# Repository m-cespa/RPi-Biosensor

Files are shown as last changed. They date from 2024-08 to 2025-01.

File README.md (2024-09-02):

# Python Package Installation:

(python packages were all installed to a virtual environment, see [1](https://learn.adafruit.com/python-virtual-environment-usage-on-raspberry-pi/overview) for documentation)

create a python virtual environment:
```
sudo apt install python3-venv
python3 -m venv <insert desired environment name>
```

activate your virtual environment: (here it is called 'venv')
```
source venv/bin/activate
```
once activated:
```
pip3 install adafruit-python-shell
pip3 install --upgrade adafruit-python-shell
wget https://raw.githubusercontent.com/adafruit/Raspberry-Pi-Installer-Scripts/master/raspi-blinka.py
sudo -E env PATH=$PATH python3 raspi-blinka.py
```
system will now ask to reboot, after reboot and activation of venv:
```
pip3 install adafruit-circuitpython-ads1x15 adafruit-circuitpython-ads7830 adafruit-circuitpython-tca9548a adafruit-circuitpython-bme280 ds18b20
```
if `board` module is causing issues, try:
```
python3 -m pip install --upgrade --force-reinstall adafruit-blinka
```

# Method: (for RPI Model 3B+)

(for circuit information refer to schematic diagram [here](./docs/schematic_labelled.png))

**PCA9546** (4 Channel Multiplexer):\
The multiplexer was used to connect 4 BME280's onto 1 rpi. The multiplexer's package `adafruit-circuitpython-tca9548a` was installed to initialise multiple same address i2c device access [2](https://learn.adafruit.com/adafruit-tca9548a-1-to-8-i2c-multiplexer-breakout/circuitpython-python). The `mux` object seen in the script allowes accesss to the devices connected to each of the multiplexer's 4 channels by specifying the device's multiplexer channel connection (index of the mux object) and i2c address. The PCA9546's specifications can be found here [3](https://www.adafruit.com/product/5663).

**BME280** (Pressure, Temperature, Humidity):\
The sensor's adafruit package `adafruit-circuitpython-bme280` was installed to access the sensor class' methods [4](https://pypi.org/project/adafruit-circuitpython-bme280/). The adafruit package was used rather than the standard `bme280` package as creating instances of the `BME280` class in the adafruit package automates calibration which was convenient given multiple instances were called. If using a single BME280, it can be initialised in the script following the steps given by the `bme280` package's repository [5](https://pypi.org/project/RPi.bme280/). The `smbus2` package [6](https://pypi.org/project/smbus2/) did not need to be installed for our configuration using the multiplexer and `adafruit-circuitpython-bme280` package (for the `smbus2` method, refer to [7](https://randomnerdtutorials.com/raspberry-pi-bme280-python/)). For our purposes, the i2c initialisation steps were done for the multiplexer, and for each of the 4 entires in `mux`, the `0x76` i2c address (the BME280) was specified. Each BME280 was connected to a pair of clock (SCL) and data (SDA) pins on the multiplexer. The BME280's specifications can be found here [8](https://thepihut.com/products/bme280-environmental-sensor#:~:text=A%20tiny%20sensor%20breakout%20with,3.3V%2F5V%20voltage%20levels.).

**DS18B20** (1-Wire Temperature):\
The sensor was wired to the rpi following the steps given by [9](https://www.circuitbasics.com/raspberry-pi-ds18b20-temperature-sensor-tutorial/). The sensor's package `ds18b20` was used rather than the method outlined in [10](https://www.circuitbasics.com/raspberry-pi-ds18b20-temperature-sensor-tutorial/). The `ds18b20` package was setup following the steps given in the package's github repository [11](https://github.com/rgbkrk/ds18b20). The DS18B20's specifications can be found here [12](https://thepihut.com/products/ds18b20-one-wire-digital-temperature-sensor).

**ADS1115 & ADS7830** (4-channel * 8-channel Analogue-Digital Converters):\
The sensors were daisy chained and then connected across the same SCL/SDA pins as the PCA9546. The two devices have different addresses to each other and to the PCA9546 (`0x70` for PCA9546, `0x49` for ADS1115, `0x48` for ADS7830) and can be recognised as different inputs along the same i2c pins. To check that both multiplexer (mux) and analogue-digital converters (adc) are being read by the rpi, type `sudo i2cdetect -y 1` into the terminal and the above addresses should appear. The i2c address of the ADS1115 can be altered by connecting the ADDR pin to one of GND, VIN, SDA, SCL which will change the device address to `0x48`, `0x49`, `0x4a`, `0x4b` accordingly. A similar procedure can be done for the ADS7830 [13](https://cdn-learn.adafruit.com/downloads/pdf/adafruit-ads7830-8-channel-8-bit-adc.pdf) but for the circuit here described, the default `0x48` address was opted for.

The following lines were passed into terminal (order specific) to install the `ads1x15` (ADS1115) library:
1. `pip3 install --upgrade adafruit-python-shell`
2. `wget https://raw.githubusercontent.com/adafruit/Raspberry-Pi-Installer-Scripts/master/raspi-blinka.py`
3. `python3 raspi-blinka.py`
4. `pip3 install adafruit-circuitpython-ads1x15`\

Installation of the `ads7830` library after the above steps proved simpler now that the Adafruit_Blinka library was present. The following line was passed into terminal:
`pip3 install adafruit-circuitpython-ads7830` [14](https://learn.adafruit.com/adafruit-ads7830-8-channel-8-bit-adc/circuitpython-and-python)

{NOTE: you must not pass `pip3 install board` into terminal as this `board` module is completely separate from the `adafruit-circuitpython` library and will cause conflict, the correct package is installed via `raspi.blinka`. Concurrent explicit installation of the package can cause package failure. Further documentation on installing the `adafruit` and `blinka` packages necessary for the ADS1115 can be found here [15](https://learn.adafruit.com/circuitpython-on-raspberrypi-linux/installing-circuitpython-on-raspberry-pi). If there is an issue with `board` attempt force reinstalling Blinka with `python3 -m pip install --upgrade --force-reinstall adafruit-blinka`}

The `busio` package was also installed. Either the `busio` or `board` packages can be used to initialise i2c bus connections. The `busio` package allows for explicit intialisation of an i2c connection where the clock and data i2c pins can be specified (if a non default i2c bus is being used). The `board` package's `I2C()` method (`i2c_init = board.I2C()`) on the other hand will initialise the i2c bus using the standard clock and data pins. To enable future intialisation of non-default i2c buses, the `busio` initialisation (which still requires the `board` package) was chosen.

When creating the `ADS1115` & `ADS7830` objects, the same `i2c` argument as for the PCA9546 was passed whilst the i2c address was altered as required to specify each device. The ADS1115 was initialised in the script following the steps given by [16](https://www.instructables.com/How-to-Use-ADS1115-With-the-Raspberry-Pi-Part-1/). To avoid conflict between the `ADS1115` and `ADS7830` classes, their methods are inherently different. The `ADS7830` class allows only direct reading of the 32-bit signal which requires manual conversion to a voltage value - refer to [17](https://learn.adafruit.com/adafruit-ads7830-8-channel-8-bit-adc/circuitpython-and-python).

The ADS1115's specifications can be found here [18](https://thepihut.com/products/adafruit-ads1115-16-bit-adc-4-channel-with-programmable-gain-amplifier). The ADS7830's specifications can be found here [19](https://thepihut.com/products/adafruit-ads7830-8-channel-8-bit-adc-with-i2c-stemma-qt-qwiic).

**IR EMITTER-RECEIVER**:\
To yield a proxy measurement of solution turbidity, a pair of IR emitter and IR Photodiode were used. The WL-TIRC THT Infrared Round Waterclear was selected as an emitter (datasheet: [20](https://docs.rs-online.com/c30e/A700000007241424.pdf)) and the IR T-1 3/4 PIN Silicon Photodiode as a receiver (datasheet: [21](https://docs.rs-online.com/461d/0900766b808b25c5.pdf)), to note: the photodiode is opaque to visible light. Photodiodes were positioned at 180° and 90° (and a reference photodiode for each LED to check whether it was on) on the opposing side of the reactor beakers to measure through and deflected beams accordingly. To measure only the change in voltage across the photodiodes, an op-amp differential amplifier circuit was trialled where one photodiode would be in an isolated environment and the other exposed to IR. Due to variations in the base resistances of the photodiodes, wires and resistors, this configuration resulted in non-zero base reading output and was hence not used.

**PWM STIRRER**:\
Cooling fans with magnets were used to drive magnetic stirrer beads in each reactor beaker. The `PWM_Stirrer.py` script was run in the background to `ALL_Sensors.py` to keep the stirrers rotating at a prescribed fixed velocity modulated by using Pulse Wave Modulation (PWM) through a GPIO pin. The script uses the `RPi.GPIO` package which should be pre-installed on updated versions of Raspbian - to check this refer to [22](https://sourceforge.net/p/raspberry-gpio-python/wiki/install/).

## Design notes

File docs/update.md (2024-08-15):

Ensure rpi is running latest Raspbian os which can be found [here](https://www.raspberrypi.com/software/operating-systems/). If an older version of raspbian is already installed:\
1. Check current version by passing `cat /etc/os-release` into terminal which should display something like this:\
```
PRETTY_NAME="Raspbian GNU/Linux 11 (bullseye)"
NAME="Raspbian GNU/Linux"
VERSION_ID="11"
VERSION="11 (bullseye)"
VERSION_CODENAME=bullseye
ID=raspbian
ID_LIKE=debian
HOME_URL="http://www.raspbian.org/"
SUPPORT_URL="http://www.raspbian.org/RaspbianForums"
```

2. If the RPi is running an old version of Raspbian pass the following commands:\
```
sudo apt update
sudo apt full-upgrade
```

Alternative: install a fresh version of raspbian onto a blank ssd through the RPi imager found [here](https://www.raspberrypi.com/software/)

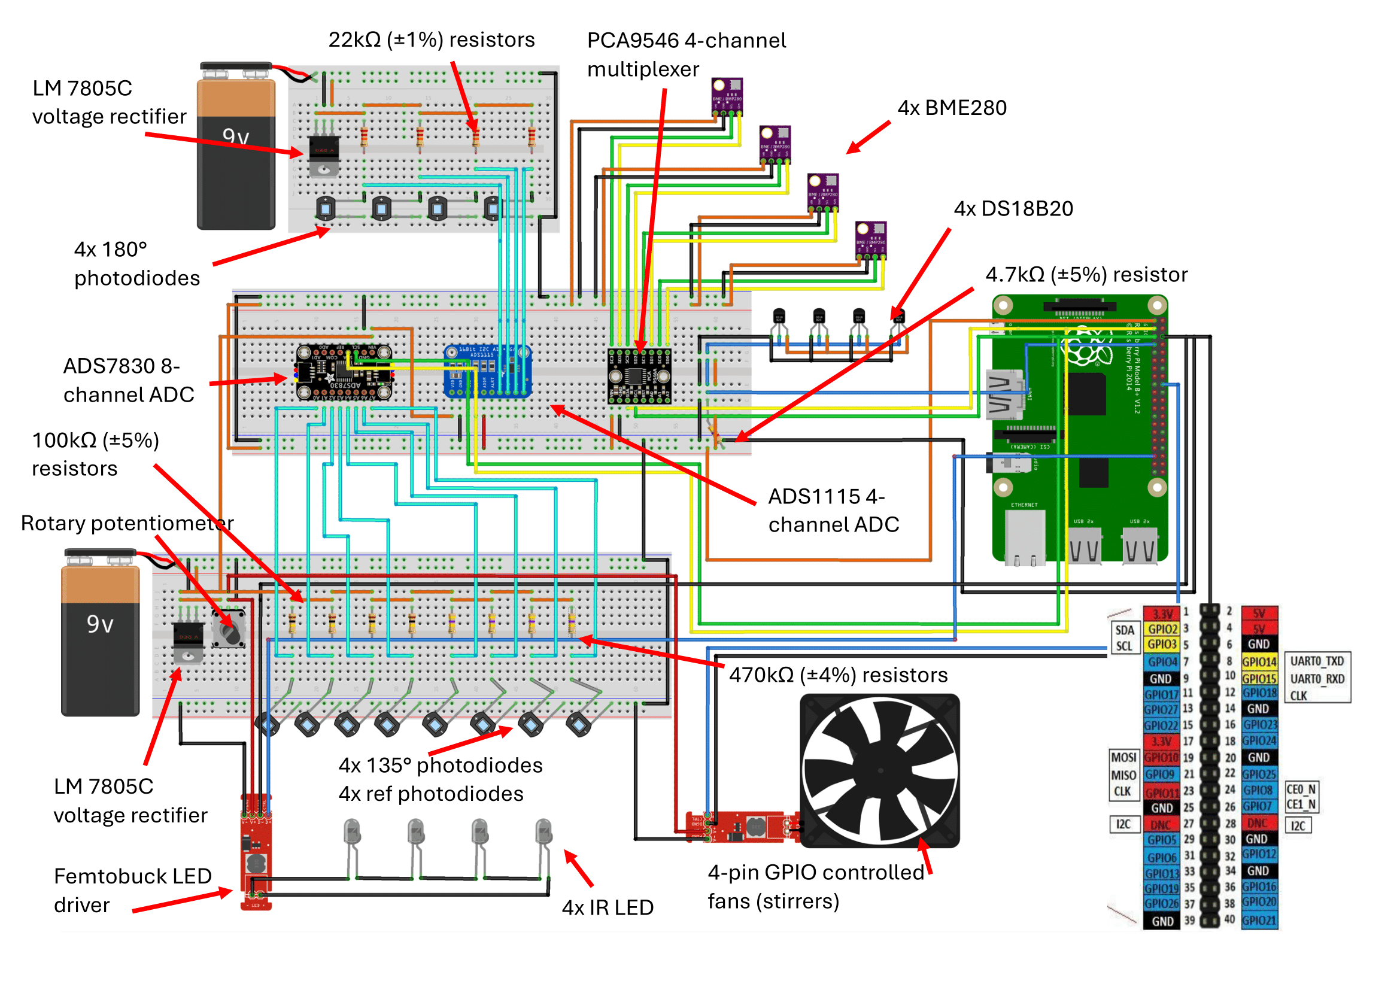
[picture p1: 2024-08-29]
docs/schematic_labelled.png

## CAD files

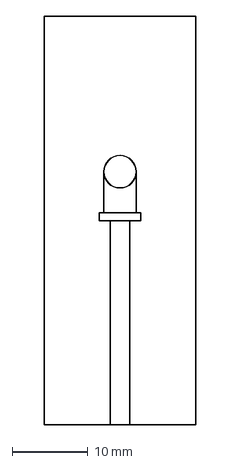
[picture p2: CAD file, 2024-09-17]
build/cad_files/photo_diode.dxf
20.0 x 54.0 mm

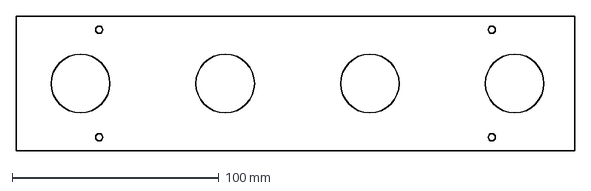
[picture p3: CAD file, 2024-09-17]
build/cad_files/lm_vial_holder.dxf
270.0 x 65.0 mm

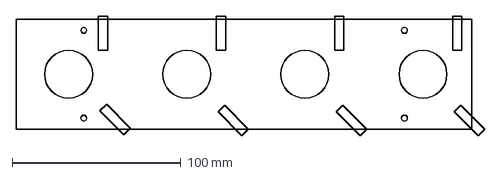
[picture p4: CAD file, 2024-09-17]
build/cad_files/higher_hole_plate.dxf
277.6 x 70.8 mm

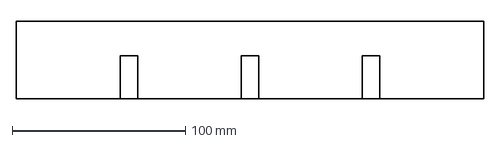
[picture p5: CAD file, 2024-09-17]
build/cad_files/slide_in_base.dxf
270.0 x 45.0 mm

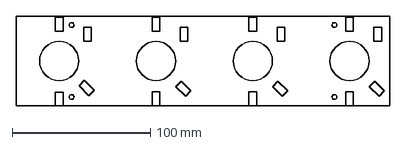
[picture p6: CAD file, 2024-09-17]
build/cad_files/top_plate_holes.dxf
270.0 x 65.0 mm

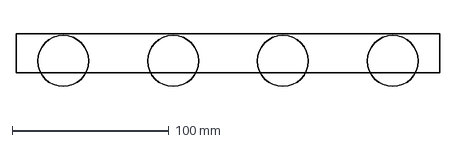
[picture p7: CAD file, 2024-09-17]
build/cad_files/light_holder.dxf
270.0 x 33.8 mm

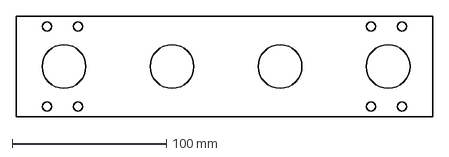
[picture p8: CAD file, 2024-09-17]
build/cad_files/lower_vial_plate.dxf
270.0 x 65.0 mm

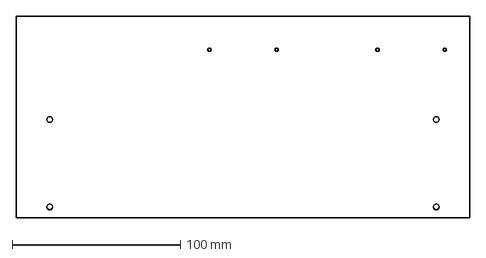
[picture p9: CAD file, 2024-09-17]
build/cad_files/clear_.base_top.dxf
270.0 x 120.0 mm

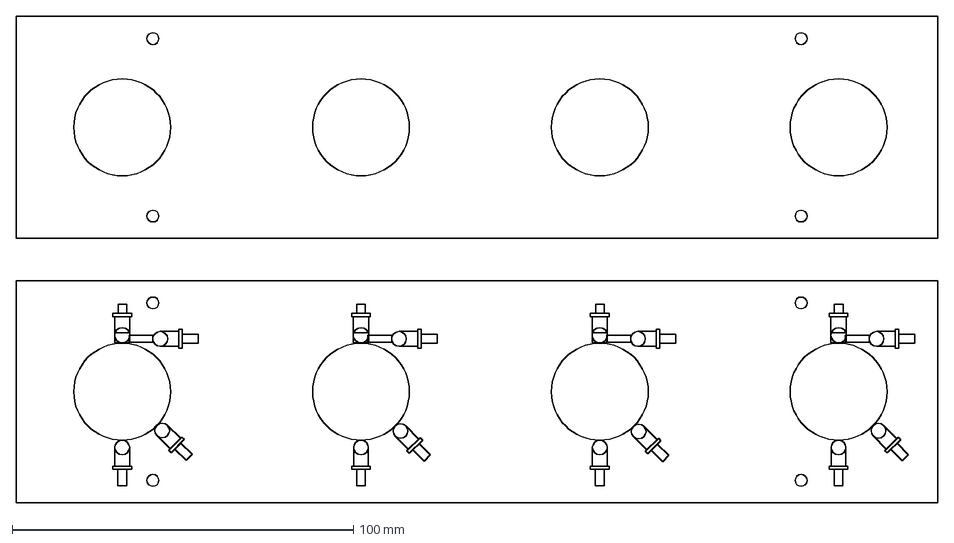
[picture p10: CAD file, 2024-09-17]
build/cad_files/photodiode_plate.dxf
270.0 x 142.5 mm

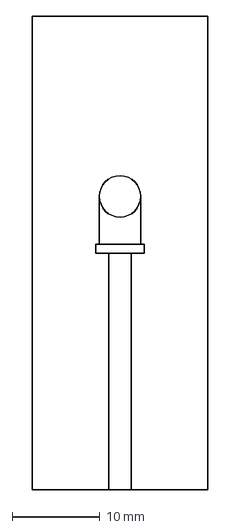
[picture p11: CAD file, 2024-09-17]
build/cad_files/LED.dxf
20.0 x 54.0 mm

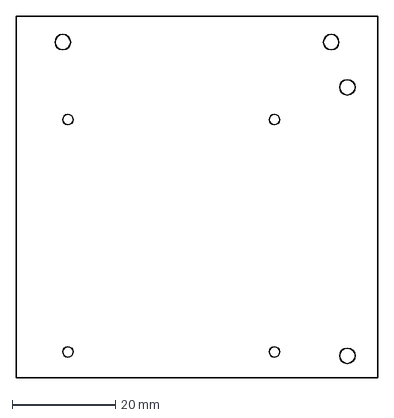
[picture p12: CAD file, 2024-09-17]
build/cad_files/pd_circuit_holder.dxf
70.0 x 70.0 mm

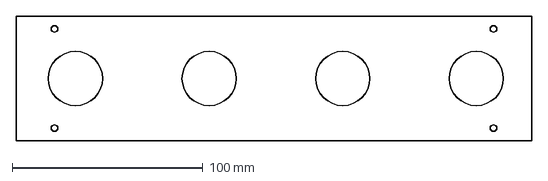
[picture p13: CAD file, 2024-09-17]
build/cad_files/therm_plate_l.dxf
270.0 x 65.0 mm

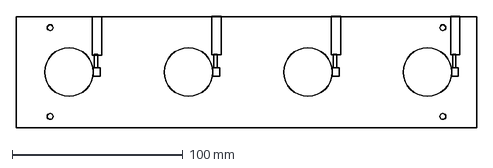
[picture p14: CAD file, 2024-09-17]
build/cad_files/therm_plate_m.dxf
270.0 x 65.1 mm

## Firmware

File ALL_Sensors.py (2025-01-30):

import time
from ds18b20 import DS18B20
from adafruit_bme280 import basic as adafruit_bme280
import board
import busio
import adafruit_ads1x15.ads1115 as ADS_1
from adafruit_ads1x15.analog_in import AnalogIn
import adafruit_ads7830.ads7830 as ADS_2
import adafruit_tca9548a
import RPi.GPIO as IO
import numpy as np
from tqdm import tqdm
from ledIO import LED_IO
import adafruit_pct2075
import matplotlib.pyplot as plt
from matplotlib.animation import FuncAnimation

# Setup the LEDs
# choosing BCM mode - other imported packages utilise it
leds = LED_IO('bcm', 37)

# MULTIPLEXER INITIALISATION
i2c = busio.I2C(board.SCL, board.SDA)
mux = adafruit_tca9548a.PCA9546A(i2c)

# init external temp sensor
#pct = adafruit_pct2075.PCT2075(i2c)
#print("Temperature: %.2f C"%pct.temperature)

# ADS1115 INITIALISATION
# through beam readings
adc_1 = ADS_1.ADS1115(address=0x49, i2c=i2c)

channels_1 = [AnalogIn(adc_1,ADS_1.P0),AnalogIn(adc_1,ADS_1.P1),
AnalogIn(adc_1,ADS_1.P2),AnalogIn(adc_1,ADS_1.P3)]

# ADS7830 INITIALISATION
# deflected and reference beam readings
adc_2 = ADS_2.ADS7830(i2c)
REF = 4.2

# BME280 INITIALISATION
bme_count = 4
bmes = [adafruit_bme280.Adafruit_BME280_I2C(mux[i], 0x76) for i in range(bme_count)]
bme_ext = adafruit_bme280.Adafruit_BME280_I2C(i2c,0x77)
print("Temperature: %.2f C"%bme_ext.temperature)

# DS18B20 INITILISATION
order = [2, 0, 3, 1]
out_temp_sensors = np.array(DS18B20.get_all_sensors())
out_temp_sensors = out_temp_sensors[order]
 
# Script start...
duration = 259200 #72 hrs
# duration = 43200 #12 hrs
# duration = 86400 #24 hrs

out_file = open('data/250130_yeast_w303_0.1xypd.txt','w')
string = """time t(s) T_{env} P_{env} T1_{ext} T2_{ext} T3_{ext} T4_{ext} 
T1 T2 T3 T4 P1 P2 P3 P4 H1 H2 H3 H4
Turb1_{180} Turb2_{180} Turb3_{180} Turb4_{180}
Turb1_{135} Turb2_{135} Turb3_{135} Turb4_{135}
Turb1_{ref} Turb2_{ref} Turb3_{ref} Turb4_{ref}"""
split = string.split()
title = ','.join(split)
out_file.write(title + '\n')


# Prepare data storage for plotting
times = []
# create empty lists to store lists of points to plot against time
vials = [[] for _ in range(5)]

# Set up the plot
plt.ion()  # Turn on interactive mode
fig, ax1 = plt.subplots(figsize=(10, 6))
live_vials = [ax1.plot([], [], label=f'Vial {i+1}')[0] for i in range(5)]

ax1.set_xlabel('Time (s)')
ax1.set_ylabel('Pressure (Vials) (mBar)')
ax1.tick_params(axis='y', labelcolor='r')

ax1.tick_params(axis='y', labelcolor='b')

plt.title('Real-time Pressure Data')
ax1.legend(loc='upper left')

# Function to update the plot
def update_plot():
    for i, line in enumerate(live_vials):
        line.set_data(times, vials[i])
    
    ax1.relim()
    ax1.autoscale_view()
    
    fig.canvas.draw()
    fig.canvas.flush_events()

with tqdm(total=duration, desc="Processing: ") as pbar:
    start = time.time()
    
    while True:
    # evaluating elapsed time at loop start effectively shifts timings by ~3s
    # this sets the time-scale at regular integer stesps
        current = time.time()
        elapsed = current - start
        
        if elapsed > (duration+1):
            print('Data recordng complete. Terminating...')
            pbar.update(duration - pbar.n)
            leds.finish()
            break
        else:
            pbar.update(elapsed - pbar.n)
            
        # turn on IR LEDs - sleep(1) to let signal settle
            leds.on()
            start_loop = time.time()
            time.sleep(1)
            try:
        # take DS18B20 readings first, reading temperature from 1-wire source file is the slowest operation
                out_temps = []
                out_temps.append(bme_ext.temperature)
                out_temps.append(bme_ext.pressure)
                for sensor in out_temp_sensors:
                    out_temps.append(sensor.get_temperature())
            # BME readings
                T_s = [bme.temperature for bme in bmes]
                P_s = [bme.pressure for bme in bmes]
                H_s = [bme.humidity for bme in bmes]
                TPH = T_s + P_s + H_s
            # voltage readings from ADCs
            # 8-channel ADC reads the raw 16-bit number, divide this by 2**8 and multiply by reference voltage (REF)
                voltages_1 = [ch.voltage for ch in channels_1]
                channels_2 = [adc_2.read(i) for i in range(8)]
                voltages_2 = [((ch / 65535.0) * REF) for ch in channels_2]
                line = f"""{current},{round(elapsed,3)},{",".join(map(str,out_temps))},{",".join(map(str,TPH))},{",".join(map(str,voltages_1))},{",".join(map(str,voltages_2))}"""
            except:
                line = f"""{round(elapsed,3)},{",".join(['NaN']*28)}"""
            finally:
                end_loop = time.time()
                
                # turn off IR LEDs
                leds.off()
                
                # Update plot data
                times.append(elapsed)
                for i, pressure in enumerate(P_s):
                    vials[i].append(pressure)
                vials[4].append(bme_ext.pressure)
            
            # Update the plot
                update_plot()
            
            # calculates correct pausing time
                diff = end_loop - start_loop
                dt = max(np.ceil(diff),diff) - diff
                pausing = dt + diff
                out_file.write(line + '\n')
                
            # sets interval between measurements
                interval = 30
                time.sleep(interval - pausing + dt)
    pbar.close()
out_file.close()

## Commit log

2024-08-14 Added circuit schematic
2024-08-30 updated ledIO.py
2024-09-02 added ledIO library
2024-09-13 added external PCT2075 temperature sensor
2024-09-17 added cad files to build folder
    [LED.dxf, clear_.base_top.dxf, higher_hole_plate.dxf, light_holder.dxf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]
2024-10-04 temperature controller
2024-10-04 failed temperature run
2024-10-07 fixed temperature 37
2024-10-11 temperature training 2
2024-10-18 pressure test 2024.10.16
2024-10-21 replace pct with bme280 for external pressure monitoring
2024-10-22 o-ring pressure test
2024-11-08 pressure test metal caps
2024-11-11 parafilm metal pressure test
2024-11-13 incubator pressure
2024-12-18 4 amodo sensor pressure test
2024-12-23 amodo second test pressure sealing
2025-01-20 yeast strain W303 (single colony resuspension) in 20ml 0.1x YPD (autoclaved in 40ml vial)
